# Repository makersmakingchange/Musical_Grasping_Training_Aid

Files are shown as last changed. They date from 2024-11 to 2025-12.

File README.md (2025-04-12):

# Musical Grasping Training Aid

## Overview

The Musical Grasping Training Aid is an assistive technology device that plays music when the device is grasped and pauses when it is let go. The user may upload their selection of songs onto the microSD card inside the device.

The device is comprised of off-the-shelf electronics and 3D printed parts.

The Musical Grasping Training Aid is open assistive technology (OpenAT). Under the terms of the open source licenses, the device may be built, used, and improved upon by anyone.

The overall cost of materials is about $90 (plus $5 for component shipping).

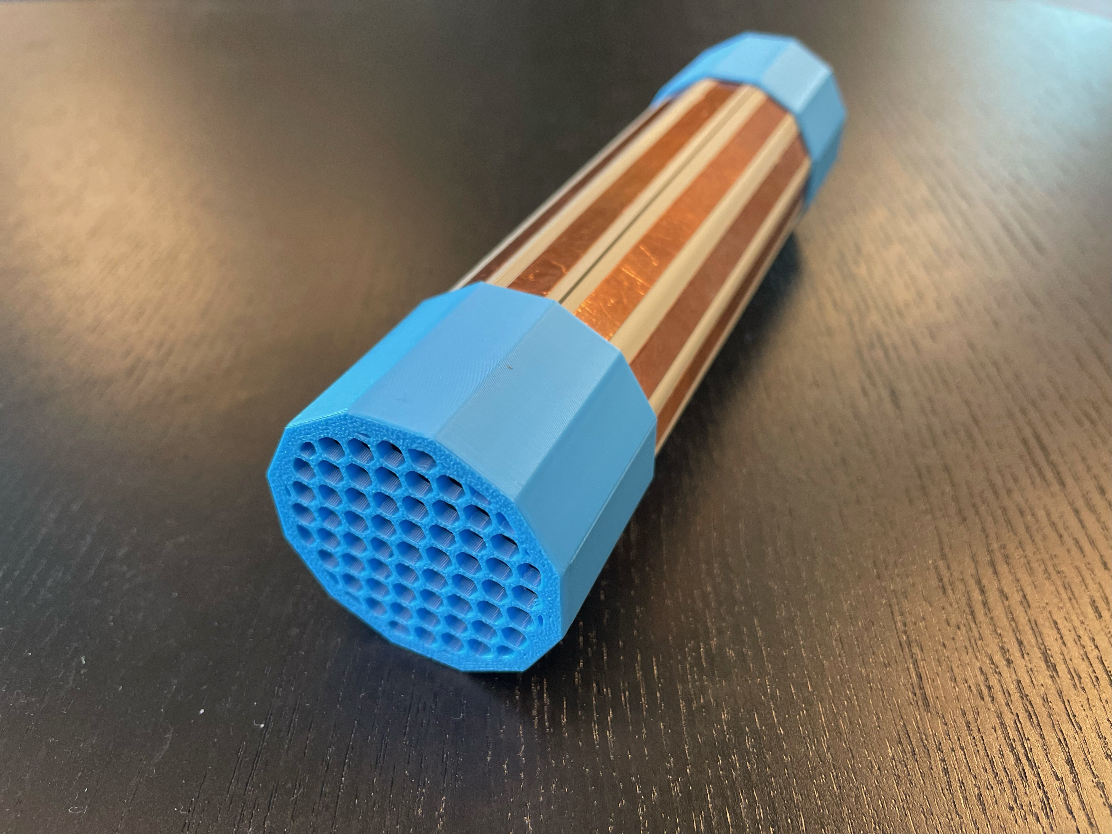
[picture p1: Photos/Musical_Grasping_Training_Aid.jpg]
Picture of Musical Grasping Training Aid.


## Makers Making Change Assistive Device Library
 - https://www.makersmakingchange.com/s/product/musical-grasping-training-aid/01tJR000007kNIXYA2

## How to Obtain the Device
### 1. Do-it-Yourself (DIY) or Do-it-Together (DIT)

This is an open-source assistive technology, so anyone is free to build it. All of the files and instructions required to build the device are contained within this repository. Refer to the Maker Guide below.

### 2. Request a build of this device

You may also submit a build request through the [Makers Making Change Assistive Device Library Listing](https://www.makersmakingchange.com/s/product/musical-grasping-training-aid/01tJR000007kNIXYA2) to have a volunteer maker build the device. As the requestor, you are responsible for reimbursing the maker for the cost of materials and any shipping.

### 3. Build this device for someone else

If you have the skills and equipment to build this device, and would like to donate your time to create the device for someone who needs it, visit the [MMC Maker Wanted](https://makersmakingchange.com/maker-wanted/) section.

## Build Instructions

### 1. Read through the Maker Guide

The [Maker Guide](/Documentation/Musical_Grasping_Training_Aid_Maker_Guide.pdf)  contains all the necessary information to build this device, including tool lists, assembly instructions, programming instructions and testing.

### 2. Order the Off-The-Shelf Components

The [Bill of Materials](/Documentation/Musical_Grasping_Training_Aid_BOM.csv) lists all of the parts and components required to build the device.

### 3. Print the 3D Printable components

All of the files and individual print files can be found in the [/Build_Files/3D_Printing_Files](/Build_Files/3D_Printing_Files/) folder.

### 4. Assemble the Musical Grasping Training Aid

Reference the Assembly Guide section of the [Maker Guide](/Documentation/Musical_Grasping_Training_Aid_Maker_Guide.pdf) for the tools and steps required to build the device.

## How to improve this Device
As open source assistive technology, you are welcomed and encouraged to improve upon the design. 

## Files
### Documentation
| Document             | Version | Link |
|----------------------|---------|------|
| Design Rationale     | 1.0     | [Musical_Grasping_Training_Aid_Design_Rationale](/Documentation/Musical_Grasping_Training_Aid_Design_Rationale.pdf)     |
| Maker Guide          | 1.0     | [Musical_Grasping_Training_Aid_Maker_Guide](/Documentation/Musical_Grasping_Training_Aid_Maker_Guide.pdf)     |
| Bill of Materials    | 1.0     | [Musical_Grasping_Training_Aid_Bill_of_Materials](/Documentation/Musical_Grasping_Training_Aid_BOM.csv)     |
| User Guide           | 1.0     | [Musical_Grasping_Training_Aid_User_Guide](/Documentation/Musical_Grasping_Training_Aid_User_Guide.pdf)    |
| Changelog            | 1.0     | [Changelog](CHANGES.txt)     |

### Design Files
 - [CAD Files](/Design_Files/CAD_Design_Files)

### Build Files
 - [3D Printing Files](/Build_Files/3D_Printing_Files)
 - [Firmware Files](/Build_Files/Firmware_Files)

## License
Copyright (c) 2024-2025 Neil Squire / Makers Making Change.

This repository describes Open Hardware:
 - Everything needed or used to design, make, test, or prepare the Musical Grasping Training Aid is licensed under the [CERN 2.0 Weakly Reciprocal license (CERN-OHL-W v2) or later](https://cern.ch/cern-ohl ) .
 - All software is under the [GNU General Public License v3.0 (GPL-3.0)](https://www.gnu.org/licenses/gpl.html).
 - Accompanying material such as instruction manuals, videos, and other copyrightable works that are useful but not necessary to design, make, test, or prepare the Musical Grasping Training Aid are published under a [Creative Commons Attribution-ShareAlike 4.0 license (CC BY-SA 4.0)](https://creativecommons.org/licenses/by-sa/4.0/) .

You may redistribute and modify this documentation and make products using it under the terms of the [CERN-OHL-W v2](https://cern.ch/cern-ohl).
This documentation is distributed WITHOUT ANY EXPRESS OR IMPLIED WARRANTY, INCLUDING OF MERCHANTABILITY, SATISFACTORY QUALITY AND FITNESS FOR A PARTICULAR PURPOSE.
Please see the CERN-OHL-W v2 for applicable conditions.

Source Location: https://github.com/makersmakingchange/Musical_Grasping_Training_Aid

## Attribution

The device was designed by Neil Squire Society / Makers Making Change. An [initial design](https://github.com/dbhaig/Musical_Toy) was created by Don Haig.

This design incorporates several commercially available open source hardware components from [Adafruit](https://www.adafruit.com/) and [DFRobot](https://www.dfrobot.com/). The Musical Grasping Training Aid firmware utilizes the [Arduino](https://www.arduino.cc/) development platform, and multiple libraries developed and shared by the open source community.

The documentation template was created by Makers Making Change / Neil Squire Society and is used under a CC BY-SA 4.0 license. It is available at the following link: [https://github.com/makersmakingchange/OpenAT-Template](https://github.com/makersmakingchange/OpenAT-Template)

### Contributors
 - Didi Dimitrova
 - Derrick Andrews
 - Stephan Dobri
 - Brad Wellington
 - Jake McIvor

----

<!-- ABOUT MMC START -->
## About Makers Making Change
[Makers Making Change Logo](https://www.makersmakingchange.com/)

Makers Making Change is a program of [Neil Squire](https://www.neilsquire.ca/), a Canadian non-profit that uses technology, knowledge, and passion to empower people with disabilities.

Makers Making Change leverages the capacity of community based Makers, Disability Professionals and Volunteers to develop and deliver affordable Open Source Assistive Technologies.

 - Website: [www.MakersMakingChange.com](https://www.makersmakingchange.com/)
 - GitHub: [makersmakingchange](https://github.com/makersmakingchange)
 - Bluesky: [@makersmakingchange.bsky.social](https://bsky.app/profile/makersmakingchange.bsky.social)
 - Instagram: [@makersmakingchange](https://www.instagram.com/makersmakingchange)
 - Facebook: [makersmakechange](https://www.facebook.com/makersmakechange)
 - LinkedIn: [Neil Squire Society](https://www.linkedin.com/company/neil-squire-society/)
 - Thingiverse: [makersmakingchange](https://www.thingiverse.com/makersmakingchange/about)
 - Printables: [MakersMakingChange](https://www.printables.com/@MakersMakingChange)

### Contact Us
For technical questions, to get involved, or to share your experience we encourage you to [visit our website](https://www.makersmakingchange.com/) or [contact us](https://www.makersmakingchange.com/s/contact).
<!-- ABOUT MMC END -->

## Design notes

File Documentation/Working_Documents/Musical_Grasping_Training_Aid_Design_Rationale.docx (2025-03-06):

# Introduction

Intentional grasp is an important developmental milestone for children. Toys that reward intentional grasping and holding could help with developing intentional grasping in various situations. An end-user requested a device which would reward grasping and holding the device, particularly by playing music while it is being held and stopping when it is put down.

This device can be for any user who is learning unimanual or bimanual coordination and grasping.

# Research

## Existing Commercial Options

Title | Baby Einstein Take Along Tunes
Link | https://www.amazon.ca/stores/BabyEinstein-Canada/page/9536BE3F-2738-48D2-830A-5A402E28861F?ref_=ast_bln
Author | https://www.kids2.com/pages/baby-einstein
License | Proprietary (Not open source)
Cost | $14.99 CDN (Amazon)
Notes | This toy does not sense when it is being held, just when buttons are pressed.

## DIY Designs

No comparable DIY designs were located.

# Requirements

## Goals

G01 | To motivate someone to pick up and hold an object by playing music while the object is being held.
G02 | Lightweight
G03 | Robust

## Functional Requirements

F01 | The device must be completely self contained (sound comes out of the device)
F02 | The device must play music when being held and stop when not being held
F03 | Users must be able to load their own music onto the device.
F04 | The device must be small enough for a child to hold (no larger than a toilet paper roll)
F05 | The device must be light enough for a child to hold

## Non-functional Requirement

NF01 | The device should be rugged enough to handle being dropped and possibly thrown by small children

## Constraints

C01 | Battery must deliver 5V (or just over) as lower voltages will be incapable of producing sufficient volumes in an audio amplifier, or audio module.

# Initial Design – Musical Toy

This design was originally taken on as a community design project. An initial design was created.

Title | Musical Toy
Link | https://github.com/dbhaig/Musical_Toy
Author | Don Haig
License | GNU GPL v3.0
Cost | Not given
Notes | This design is the basis for the musical toy and was used as the initial proof of concept and design.

The initial design was created by Don Haig and was uploaded to GitHub (https://github.com/dbhaig/Musical_Toy). MMC staff built and tested a prototype. This version was not sent to the original requestor. The original design used an Arduino Nano, a 9V battery, a small speaker, a DFPlayer, and a wire inserted into a 3D printed enclosure. The design was made using parts the original designer had on-hand or could order quickly online.

## Touch Sensing

The device worked by using a wire wound around the enclosure as a capacitive sensor. When the device was touched/picked up, lights would turn on and music would play. When it was released, the music and lights would stop.

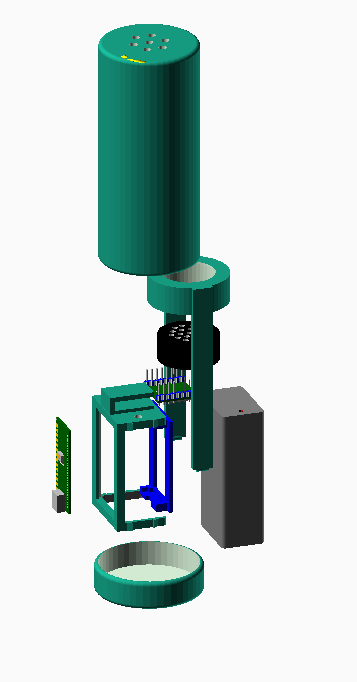
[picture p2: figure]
Exploded View

Figure 1. Exploded View

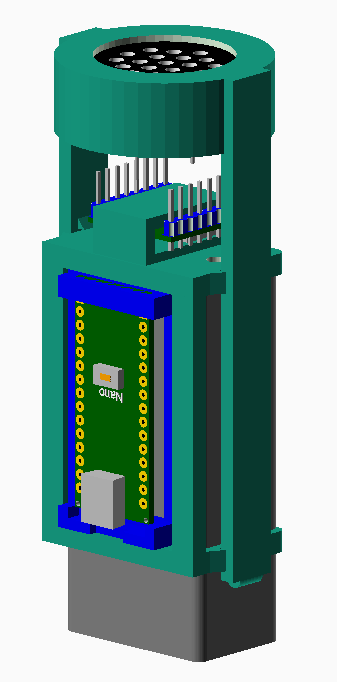
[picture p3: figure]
Interior Assembly

Figure 2. Inner Assembly

## Musical Toy Testing

The toy played music when activated, and would stop when deactivated, but the touch sensing did not work reliably. Depending on the sensitivity set within the code, it would activate before being touched (e.g., hand in proximity) or would not activate at all.

## Opportunities for Improvement

1. Use a smaller / less expensive microcontroller.
2. Using a smaller, more efficient power source than a 9V battery.
3. Inserting the wire into the case was difficult.
4. The outer enclosure is quite thin and may not be very durable.
5. Utilize a more reliable touch sensing method.

# Conceptual Design

The initial concept of the Conductive Music Player was to have a classic handheld flashlight tube shape. This tube would be small enough to be held by children, but big enough to hold batteries capable of powering the toy, for at least several hours.

## Key Functions

1. Plays Sound
2. Senses when gripped / lifted

## Playing Sound

1. DF Player Mini

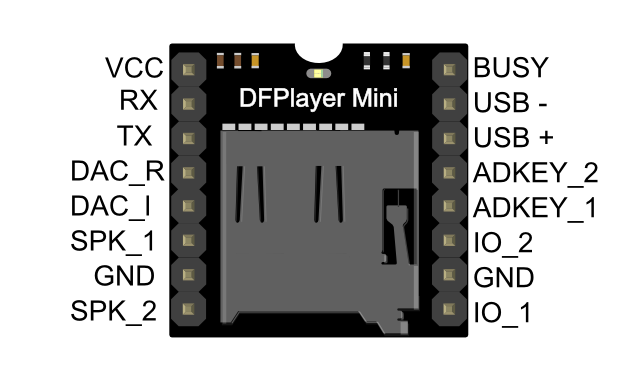
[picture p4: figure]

  - Integrated amplifier, microSD card
  - Fully supports FAT16, FAT32 file system, maximum support 32G of the TF card, support 32G of U disk, 64M bytes NORFLASH
  - A variety of control modes, I/O control mode, serial mode, AD button control mode
  - advertising sound waiting function, the music can be suspended. when advertising is over in the music continue to play
  - audio data sorted by folder, supports up to 100 folders, every folder can hold up to 255 songs
  - Low impedance speaker for good volume, with plastic cone/diaphragm for water resistance
  - Requires specific file naming
2. SD Player + Amplifier module (e.g., Open Playback Switch)
3. Adafruit Audio BFF Add-on for QT Py and Xiao
  - https://www.adafruit.com/product/5769
  - Has a built in amplifier and SD card but requires the analog pin from the microcontroller.
  - Product was not available when the project was started, but could be a good option for future improvements to the design

## Grip Sensing Method

### Capacitive Touch

1. Internal Microcontroller
2. Dedicated Module

The conductive music toy utilizes the Adafruit FreeTouch Arduino Library, which in turn, utilizes Atmel Q touch at the hardware level, on the micro controller chip.

Excerpt below, from: http://ww1.microchip.com/downloads/en/DeviceDoc/atmel-42195-qtouch-library-peripheral-touch-controller_user-guide.pdf

“Atmel® QTouch® Peripheral Touch Controller (PTC) offers built-in hardware for capacitive touch measurement on sensors that function as buttons, sliders, and wheels. The PTC supports both mutual and self-capacitance measurement without the need for any external component. It offers superb sensitivity and noise tolerance, as well as self-calibration, and minimizes the sensitivity tuning effort by the user.

The PTC is intended for autonomously performing capacitive touch sensor measurements. The external capacitive touch sensor is typically formed on a PCB, and the sensor electrodes are connected to the analog charge integrator of the PTC using the device I/O pins. The PTC supports mutual capacitance sensors organized as capacitive touch matrices in different X-Y configurations, including Indium Tin Oxide (ITO) sensor grids. In mutual capacitance mode, the PTC requires one pin per X-line (drive line) and one pin per Y-line (sense line). In self-capacitance mode, the PTC requires only one pin with a Y-line driver for each self-capacitance sensor.

Atmel® QTouch Features:

- Implements low-power, high-sensitivity, environmentally robust capacitive touch buttons, sliders, and wheels
- Supports mutual capacitance and self-capacitance sensing
- Up to 32 buttons in self-capacitance mode
- Up to 256 buttons in mutual capacitance mode
- Supports lumped mode configuration
- One pin per electrode - no external components
- Load compensating charge sensing
- Parasitic capacitance compensation for mutual capacitance mode
- Adjustable gain for superior sensitivity
- Zero drift over the temperature and VDD range
- No need for temperature or VDD compensation
- Hardware noise filtering and noise signal de-synchronization for high conducted immunity
- Atmel provided QTouch Library firmware and QTouch Composer tool”

#### Conductive Sensing Surface

Several options were considered for the conductive sensing material:

1. Conductive Cloth
2. Copper Tape
3. Embedded wire
4. Conductive paint
5. Conductive filament
6. Copper Foil

Conductive Cloth

The conductive cloth is a square of cloth plated with conductive material, such as silver. When someone touches the cloth, the capacitive touch library detects a change in capacitance of the cloth. The cloth offers low resistance (1 Ohm per foot of cloth), so the circuit can be more sensitive to touch. Additionally, the large surface area of the cloth allows the circuit to be more sensitive and reliable, as it is less likely that outside electromagnetic noise will influence the circuit than with embedded wires, which act like antennae. The conductive cloth also provides a soft surface for someone to touch, which may be desirable for some users. The cloth can be washed and cleaned as necessary.

Copper Tape

The copper tape is a roll of adhesive copper tape that will be stuck on the outer surface of the device to sense touch. When someone touches the tape, the capacitive touch library detects a change in capacitance of the tape. The copper tape is very thin and flexible allowing it to follow the surface shape.

Embedded Wire

The embedded wire follows a similar design to the copper tape, however, instead of being a flat adhesive strip it is a wire. The wire is sturdier and not as fragile as the tape, so it is more durable and can take on rough handling. The embedded wire would be attaches through small grooves into the device enclosure. Strips of wire can be attached to create a larger activation surface; however, it is important to be cautious that the embedded wire does not act like an antenna.

Conductive Paint

The conductive paint is a mixture of paint and carbon which creates a conductive coating on a surface. The paint is easy to apply with a brush, however, is difficult to clean and may chip away with long term use and rough handling.

Conductive Filament

Conductive filament is 3D printing filament that has combines a base plastic such as PLA with conductive additives to create a 3D printed conductive material. Unlike the other options listed, the conductive filament does not require anything to be attached to the outer surface of the device, as the enclosure itself will be conductive. The change in capacitance is sensed from the large activation surface of the device body. As conductive filament is not very common, this is reflected in the higher price point per roll of filament.

Copper Foil

Similar to the copper tape, the copper foil is a thin and flexible copper surface however, it does not have an adhesive surface. As the copper foil is a large copper sheet, it can be cut to the desired size and even wrapped along the entire outer surface if needed to. To attach the copper foil to the device, glue or another securing method will need to be used.

The conductive cloth offered a larger sensing surface area, which also increases sensitivity of the capacitive sensing.

### Linear soft potentiometer

A linear soft potentiometer was also considered for sensing touch. The potentiometer worked as a voltage divider and would output a different voltage based on where along its length the user was touching. The output voltage was 1/3 to 2/3 VCC.

https://www.adafruit.com/product/178

### Accelerometer

An accelerometer

#### LIS3DH

- Three axis sensing
- ±2g/±4g/±8g/±16g selectable scaling
- Both I2C (2 possible addresses) and SPI interface options
- Interrupt output
- Multiple data rate options 1 Hz to 5Khz
- As low as 2uA current draw (just the chip itself, not including any supporting circuitry)
- Tap, Double-tap, orientation & freefall detection

#### Accelerometer Additional Use Cases

As the accelerometer can sense varied motions with angle positions, and the micro controller can differentiate between them, it becomes possible to change device settings and behaviours based on this. As an example, the angle at which the device is positioned upon start up, can allow a user to set the sound to a specific volume. This can save parts in the product design, and the associated space and monetary costs those entail.

The ability to sense different user motion types should allow for various product behaviors, including:

- Setting volume (angle on device startup).
- Changing to a new song (shaking the device)
- Stepping up or down through a song list, or other list. (tilting device left or right)

Note that while using these methods can reduce device complexity and parts count, investments in software development, both in time and money, will be required upfront.

### Power Source

The toy was designed to be powered by battery, so it was portable. Disposable batteries were chosen for the initial design for simplicity. To meet the voltage demands of the electronics, four AAA batteries were used to supply 6V, and a voltage regulator was used to step this down to 5V for the electronics.

## Concept A: DF Player Mini + Accelerometer

Concept A used the DF Player Mini to read the SD card and play songs, and an accelerometer (Adafruit LISD3H) to sense when the toy was being held. The idea was to have the firmware track the stability of the readings from the accelerometer to differentiate between the toy sitting or lying stationary on a surface or being held. The assumption would be that even when a user was holding the toy still that the readings from the accelerometer would be more variable than when it was sitting or lying on a surface.

## Concept B: DF Player Mini + Capacitive Touch

Concept B was most similar to the original design by Don Haig but changed the method of capacitive sensing. Rather than using a wire wrapped around the case, a strip of copper tape and/or a conductive cloth is used for capacitive sensing.

## Concept C: DF Player Mini + Linear Soft Potentiometer

Concept C used a linear soft potentiometer to sense touch. The potentiometer worked as a voltage divider and would output a different voltage based on where along its length the user was touching. The output voltage was 1/3 to 2/3 VCC.

## Concept D: DF Player Mini + Capacitive Touch +Accelerometer

Concept D built off the original design by Don Haig. It used the DF Player Mini to read the SD card and play songs, and used capacitive touch sensing to detect when it was being held, and an accelerometer for extended options (such as changing songs). The accelerometer was used with tilting to change to the next or previous song based on how the accelerometer was tilted.

## Concept Selection

Concept D was selected for the prototype. We chose to include the accelerometer and capacitive touch sensing to increase future capabilities of the toy. The software for the capacitive touch sensing was simpler to develop and troubleshoot than it would have been to create the touch sensing with the accelerometer, but the accelerometer will allow for more complex controls and use cases in future developments with updates to the firmware.

The capacitive touch system was chosen over the linear soft potentiometer to increase the sensing surface of the toy. Either the soft potentiometer or using only a strip of copper tape would require a user to touch a smaller area of the toy to start it playing music. Using the conductive cloth allowed us to wrap more of the toy and decrease the likelihood of a user grasping the toy without activating it by missing the sensor. Additionally, the larger surface area increased the sensitivity and reliability of the capacitive sensing. The large piece of cloth was also the same price as the single linear soft potentiometer, and required only one resistor instead of three, decreasing the complexity of the circuitry and potential for errors when building the toy.

# Detailed Design

## Schematic

Add wire for conductive cloth (or copper tape) and a player busy line, to limit microcontroller interruptions.

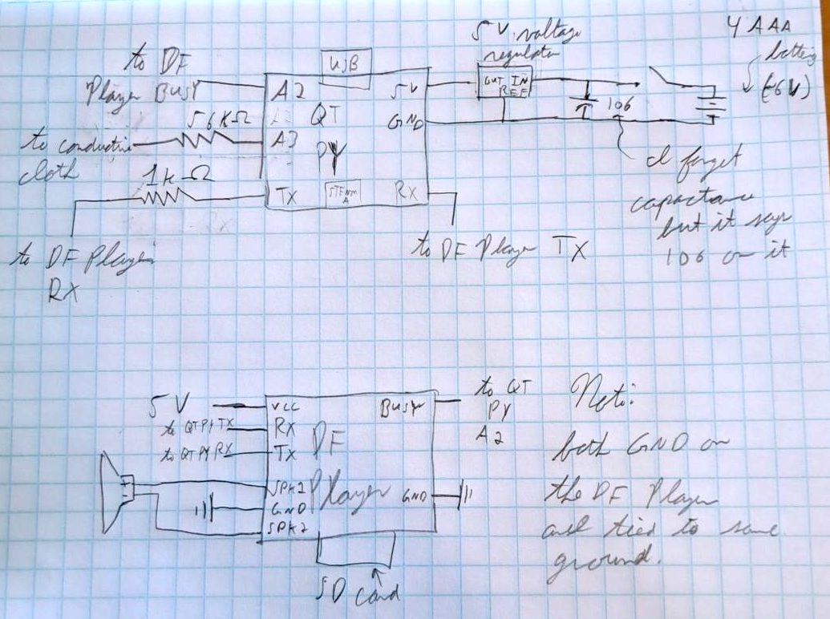
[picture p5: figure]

Figure 3. Schematic Sketch. Stephan Dobri.

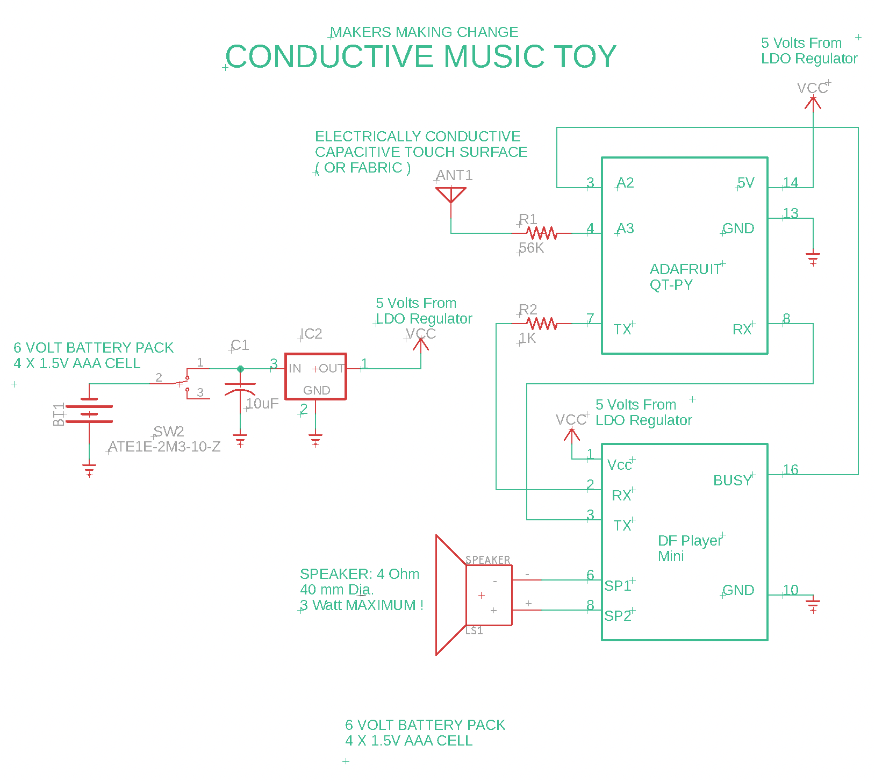
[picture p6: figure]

Figure 4. Electrical Schematic.

## Component Selection

### Microcontroller

Adafruit QTPY SAMD21

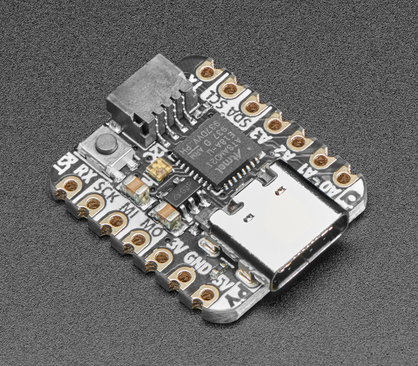
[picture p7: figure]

Figure 5. Adafruit QTPy SAMD21. CC SA-BY. https://learn.adafruit.com/assets/95170

### Speaker

Choosing the speaker for this design was relatively straightforward as the battery constraints and low voltage circuitry necessitates the use of low impedance speakers. Low impedance speakers are typically only available in 4 ohms, and 8 ohms from manufacturers. For a design, running on 3 to 5 V circuitry, 4 ohms is clearly the best choice, as higher voltages are required to drive 8 ohm speakers to a suitable volume level. As for physical size, a 40 mm speaker was chosen, as larger speakers would mean the toy would become too large for handheld use. The final choice was to use a plastic cone speaker rather than a paper cone, as a plastic cone can withstand water, and water-based, cleaners.

### Sound Module

The DFPlayer mini was chosen due to its sub miniature size, built-in 3 W audio, amplifier, and ability to be controlled by Arduino type microcontrollers. Additionally, the DFPlayer mini can except a microSD card within its own microSD card slot. This means that no external SD card reader is required. Finally, the DFPlayer is a very low cost, coming in at under $10.

The Sound Module connects to the microcontroller using a serial connection.

### Power Source Selection

The choice was made to go with a 6 V battery pack comprised of four AAA batteries. Batteries were an obvious choice, as the design is for a toy that will be carried around by small children. AAA batteries are available from most shops in both rechargeable and non-rechargeable types and are considered safer than lithium type batteries. Other readily available batteries, such as C and D type cell, are too large and heavy for a small carry around toy. The quantity of cells needed is determined by the volt, the voltage requirement of the circuitry. In this case, both the micro controller and the DFPlayer mini can be powered by 5 V. While the microcontroller can be driven by as little as 3 V, the DFPlayer requires a minimum of 5 V. Furthermore, battery ageing needs to be considered, so it’s better to start with a slightly higher voltage and regulate down to the desired voltage. In this manner, the circuit voltage remains stable. A small three pin 5V LDO regulator was chosen to trim the small excess voltage from the battery. An LDO (Low Drop Out) type regulator was chosen, as traditional voltage regulators usually stop working when the input voltage drops below the regulated output voltage. This allows the battery voltage to drop down to 4.5 V (the minimum required by the DFPlayer module) before the circuit stops working

### On/Off (power) switch

The slide switch was chosen to be as small as possible to be operated by a human finger. A 1-amp switch was chosen, as the circuitry in the Conductive Music Toy uses less than an amp. Larger switches would only be heavier and more expensive. An SPDT (Single Pole Dual Throw) type switch was selected, as it has a minimum of contacts to solder, while still being able change which side of the switch is considered as on or off.

### Accelerometer

The LISDH accelerometer from Adafruit was chosen for its low cost (under $10), small form, factor and ready availability from both Digi Key and Mauser electronics suppliers. While there are many suppliers that provide accelerometers with this description, we found that only the Adafruit version allows the device to be connected to a microcontroller via a solderless STEMMA type cable. This saves eight solder joints and the associated chance of wiring mistakes being made.

## Enclosure Design

### Shape

12 -sided

- Prevents rolling
- Feels more like a rounded handle

## Conductive Sensor

### Conductive Cloth Physical Attachment

The first design for attaching the cloth to the enclosure was to use metal snap fasteners. Two snaps would be attached to the enclosure, and the other snaps would be sewn onto the cloth. A wire was soldered to one of the snaps and ran into the enclosure to the 56k Ohm resistor in the above schematic, providing the electrical connection to the cloth. While the electrical connection worked with this method, the snaps could not hold two layers of cloth between them and would pop open very easily, so this method was abandoned.

The second method was to use adhesive backed hook and loop fasteners to attach the cloth to the enclosure. The adhesive backing was used to attach the fastener to the enclosure and onto the cloth. The cloth could then be attached to and wrapped around the enclosure. Since the cloth is difficult to solder, the electrical connection is created by a strip of copper tape on the outside of the enclosure to which the wire leading to the resistor is soldered. This method proved effective for the time being and is implemented in the prototype. There needs to be some long-term testing to assess how well the adhesive sticks to the cloth over time.

### Conductive Cloth Electrical Attachment

Wires soldered to snap

### Clothes vs. Tape

Cloth

- More to difficult to attach to handle
- More difficult to attach the electrical connection
  - Punch and snap required specialized hardware
  - Stainless steel conductive cloth hard to solder to
- Need to wrap around the enclosure – harder to open two-part split enclosure
- More difficult to clean

## Firmware

### Capacitive Touch Calibration

1. Sets baseline when first powered
2. Compares current value to adjustable threshold
3. Adjusting Volume

# V0.1 – Minimum Viable Product

## Summary

1. Total cost
2. Total print time / total number of printed components
3. (estimated assembly time)

## Features

1. Slide switch for controlling power
2. 4 internal AA batteries for power
3. 4 M3 screws to secure enclosure
4. Code adjustable volume
5. Supports 32GB SD card
6. Grasp and Play Operating Mode

### User Interface

Primary User

1. Lift to play music

Secondary User

2. Control power
3. Add / change songs by opening and modifying files on SD Card

Code

4. Adjust volume
5. Adjust capacitive touch sensitivity

### Operating Modes

1. Grasp and Play
  1.1. Cycling power resets to first file
  1.2. Grasping toy will cause music to play
  1.3. If grasped long enough, will cycle to next song
  1.4. If dropped, music will pause
  1.5. If grasped again, music will un-pause

## Internal testing

Testing while on battery power.

## Testing

(Any specific questions to address testing?)

1. Volume? Is there a need to adjust the volume
2. Adjusting volume with a potentiometer feeding an analog input.

## Opportunities for Improvement

1. Recess power switch?
2. Consider more secure cloth attachment method (integration into case, copper tape, glue, etc)
3. Recess enclosure-fastening screws
4. Simplify method / number of screws for opening enclosure
5. Investigate printability of sliding rails
6. Add accelerometer functionality

# V0.2 – Third Party Capacitive Touch Chip

Touch Sensor –

## Testing

3. Works on battery
4. Works by attaching wire from third party breakout board to copper tape on holder
5. (40 second recalibration time?)

# V0.3 – Third Party Capacitive Touch Chip

## Component Selection

### Touch Sensor – Adafruit MPR121 Module

The Adafruit MPR121 is a 12-channel capacitive touch sensor module with an I2C interface. The module is based on the MPR121 IC by Freescale Semiconductor. Intended for MP3 players, and other low-power, hand-held electronics. Power consumption for this chip is extremely low, coming in at 29 μA average supply current.

MPR121 Fact sheet: https://www.nxp.com/docs/en/fact-sheet/MPR121FS.pdf

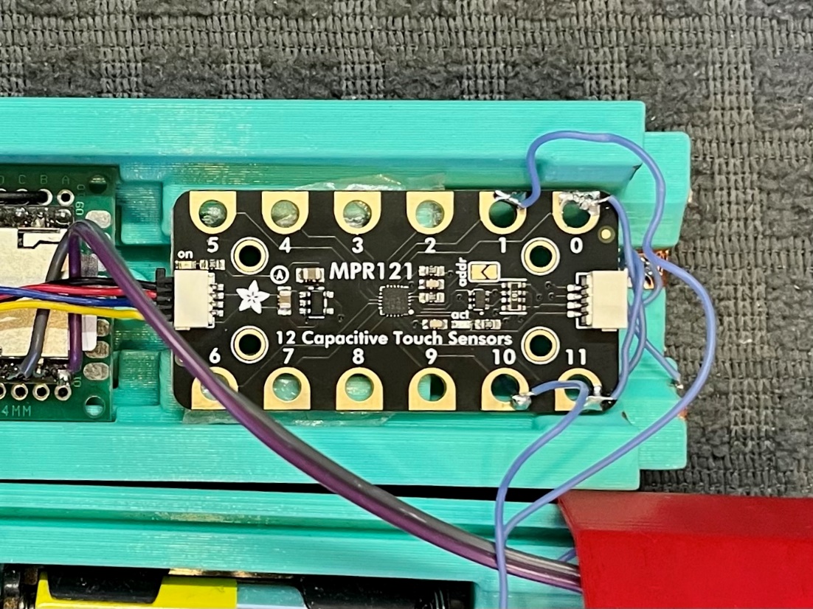
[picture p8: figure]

MPR 121 Module wiring:

The Adafruit MPR 121 module is connected to the QT-PY micro via a standard Stemma cable, which carries the basic I2C bus wires (Black=GND, Red =VCC Blue = Data Yellow = CLKor clock) The music toy has a set of 12 adhesive copper strips for touch sensing. The strips are wired together in four sets of three. A wire from each quadrant is then connected to one of the 4 input pads of the MPR-121.

Testing Questions

1. Activation on touch vs proximity? The Adafruit module activates, only on touch based on the testing that was done with the conductive music toy. This was done by approaching a finger to a capacity sensor pad and noting that the sensor did not trigger, even when the finger was within a millimeter of the touchpad. It was found that activation could occur through very thin paper or plastic material, however this this still “physical contact” sensation for a human finger.
2. Activation on contact vs grasp vs lifting? It is expected to be possible to differentiate between touching and grasping by taking advantage of multiple sensor, input, lines of the MPR 121. A single touch is unlikely to trigger multiple input lines simultaneously. A single touch is unlikely to trigger multiple input lines simultaneously. Therefore, grasping by hand can be assumed, if multiple input lines are triggered.

### Opportunities for Improvement

1. Modify enclosure
2. Add On/off label
3. External / easier access for MicroSD card?
4. Add accelerometer to better determine between grasping and lifting

### User Testing

The most recent version of the Conductive Music Toy was built and sent to the original requester, 4 years after the request was made. In the interest of getting, it to the tester as soon as possible, no changes were made to the SCAD enclosure to increase makeability. The existing enclosure was altered with a Dremel after printing to accommodate the parts, and it had to be fully glued shut once assembled.

A quick, basic, software implementation was written that covers the basic operating loop that the tester asked for, without any advanced grip detection or other advanced features.

### Maker Feedback

- Solder joints to copper tape are difficult and fragile
- Enclosure needs more room for wires/connections between components
- Enclosure needs a bit more tolerance between parts, especially when things such as copper taper are being inserted between them

### User Feedback

“Hi,

I'm sending a quick update with some feedback on the fun conductive music toy you've sent us for trial with my client - thank you again so much for hearing me out, finding a way to make this crazy idea happen and being open to feedback along the way.

Key observations so far:

-the size and shape seem pretty good. The diameter works fine for her hand - it's about the size of her hand railing on the stairs so works pretty well. I was initially a little worried it might be heavy for her but thus far she's not holding it independently and I suspect she can navigate it okay once she's really sustaining her grasp longer to carry it with her. Probably wouldn't want it to be too much heavier.

-sound level: it's a bit loud - we stuck a sock on the end at times to lower the volume

-music loaded: it took us a little while to realize that we could just hold it for a long time to get the songs to advance and change. Seems that when we turn it off, it resets to the first song. Now that we know this, we can play around with it and hold it for awhile to get it to a new song that lights up her reaction!

-touch functionality: for some reason when it's initially turned on it takes a little time to warm up and feel good about its existence - it helps to have an adult muck about with it for a few minutes to help it warm up and be responsive to her touch

wish list items:

-stand system: I'm going to try (?) to make a little stand for it to keep it in a vertical upright position as this makes it easier for her to grasp - like a docking system that allows her to pick it up in that vertical orientation. I'll probably try a little foam or cardboard - a 3D printed thingy in the future that fits would be cool. Right now, she holds it best when we hold the end portions (VERY HELPFUL feature - as this allows us to hold it up in place and NOT activate it, waiting for just HER touch to activate it).

She's most often using her hands to grasp it well when she is using it to stabilize herself - so picture that she's on a physio ball with some hands on help from me - I challenge her balance a little and she reaches out to the conductive toy to stabilize herself - I'm holding it up in the air for her to grab - she had some GREAT visual looks to it and smiles when the music activated. She needs lots of time with this to keep building her recognition of it and understanding of its cause/effect function.

-long term usage: as noted when you sent it, being able to charge the battery and change the music stored on it through a port would be great

-it'd also be great to have a way to advance the songs with a single button (for the adult to do, so not needed to be special for kid) - thinking here that her music interests change quickly and it's really helpful for her when we change the song up!

Again - I want to send a really big thank you to the team for this opportunity - it feels really good to have a new idea to support this kid, help her light up and teach her something new with something that literally does not exist out there in the world.

THANK YOU!

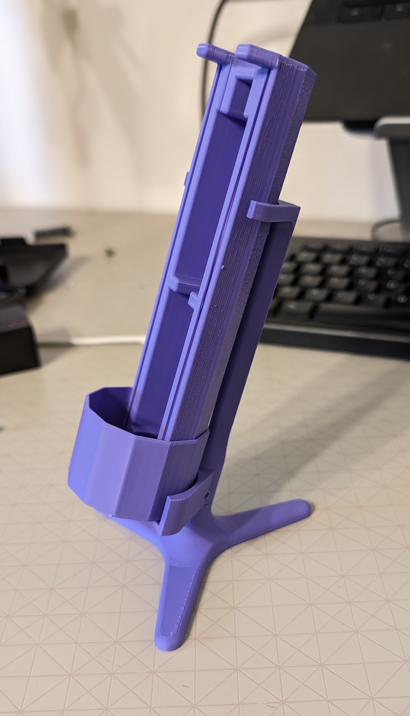
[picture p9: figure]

### Follow Up User Meeting

Brief follow up meeting with the user to talk about the feedback given and get some more detail

- Song skip button to keep it fresh
- Made a stand to hold the device upright
- Want the volume turned down a bit, but user volume adjustment is not a priority
- Startup issues may be due to users touching the tape while turning it up and skewing initial calibration

### Next Steps

- Improve enclosure
- Add ability to change batteries/charge the device
- Add the ability to change songs loaded on the device
- Add a recessed switch to skip to the next song without letting it play all the way through
- Secondary-user accessible volume control

# V1.0 Musical Grasping Training Aid

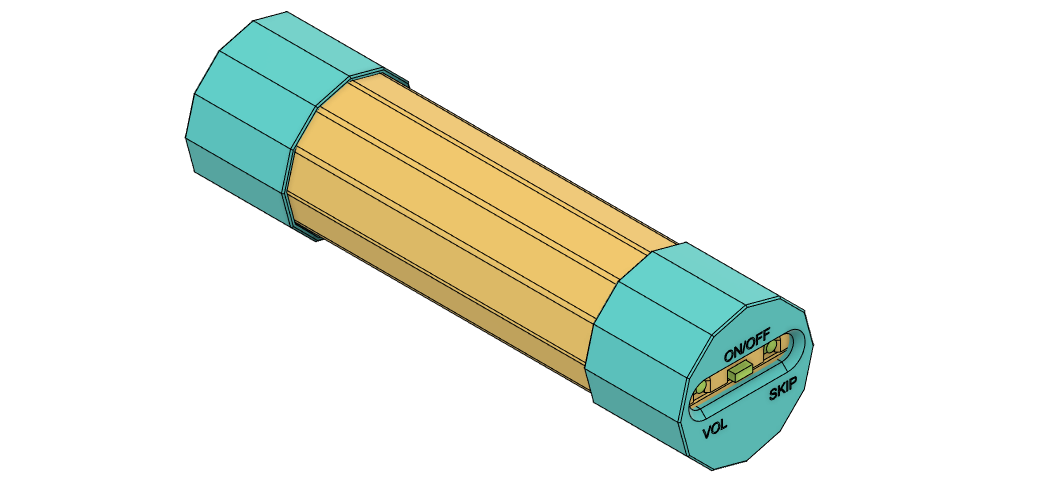
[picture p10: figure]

## Proposed Changes

1. Improve make ability and usability of enclosure
  1.1. Add ability to change batteries
    1.1.1. Integrating a commercially available battery holder
    1.1.2. Creating a 3d printed battery holder and use commercially available battery contacts
      1.1.2.1. Copper tape?
  1.2. Power switch
  1.3. Add a recessed switch so secondary user can skip to the next song
    1.3.1. (Currently the only way to advance the song is to activate the device and wait until the entire song plays)
  1.4. Secondary user access to the SD card to change songs
    1.4.1. Sufficient instructions for reasonably tech savvy user to remove SD card, connect to computer, load songs using specified numbered file format, replace SD card
  1.5. Consider adding secondary user accessible control for adjusting volume
    1.5.1. 1 button
      1.5.1.1. toggle through levels
      1.5.1.2. short press / long press
    1.5.2. 2 two buttons – volume up / volume down
    1.5.3. Potentiometer?
    1.5.4. Using the touch sensor / other existing input to control volume
  1.6. Ensure sufficient clearance for cables, etc.
  1.7. Maintain diameter
  1.8. Maintain or reduce weight
2. Documentation
  2.1. User Guide
3. Component Changes
  3.1. Bluetooth-enabled microcontroller (e.g., XIAO nrf52840)
    3.1.1. Training Aid + Smartphone App
    3.1.2. Training Aid + Bluetooth Microcontroller
  3.2. Alternate Music Player
    3.2.1. Adafruit Audio BFF Add-on for QT Py and Xiao (https://www.adafruit.com/product/5769)

## Requirements

### Goals

G01 | To motivate someone to pick up and hold an object by playing sounds while the object is being held.
G02 | Lightweight
G03 | Robust
G04 | The ability to continue to motivate the user
| A secondary user (e.g., therapist, aide, caregiver, parent) must be able to adjust some settings on the device.

### Functional Requirements

F01 | The device must be completely self contained (sound comes out of the device)
F02 | The device must play music when being held and stop when not being held
F03 | Users must be able to load their own music onto the device.
| User must be able to periodically change the music on the device.
F04 | The device must be small enough for a child to hold (no larger than a toilet paper roll)
F05 | The device must be light enough for a child to hold.
| A secondary user must be able to control the power state of the device.
| A secondary user should be able to control the volume of the device
| A secondary user should be able to skip to the next song.
| A secondary user should be able to access the device controls without the use of tools.
| The primary user should not be able to access the controls.
| The secondary user must be able to change the batteries.
| The primary user must not be able to access the batteries. | Safety
| The secondary user should be able to access the batteries without tools. | Convenience

### Non-functional Requirement

NF01 | The device should be rugged enough to handle being dropped and possibly thrown by small children

### Constraints

C01 | Battery must deliver 5V (or just over) as lower voltages will be incapable of producing sufficient volumes in an audio amplifier, or audio module.
C02
C03

## Design Features

| Version V0.3 (MVP) | Version V1.0
User Interface | On/Off Button | On / Off Button Volume Control Ability to skip songs
Battery Access | None (enclosure glued shut) | Accessible by secondary user
Capacitive Sensor Calibration | Auto-calibration (Just on startup or continuously?) | Auto-calibration
SD card Access | None (enclosure glued shut) | Accessible by secondary user

### User Interface Brainstorm

V0.3

- Power switch accessible on the end cap
- Power switch is partially recessed into the end cap

V1.0

- User interface elements

User Interface Options

1. Recessed / partially recessed into the enclosure or end cap
2. Removable or openable panel or cover that prevents the primary user from accessing them
3. ~~(~~~~Wireless / secondary device)~~

### Music Control

V0.3

- Always starts at the beginning of the playlist of songs when the device is turned on.
- There is no user control to skip songs.
- When activated, current song plays. When let go, music pauses. When unit is re-activated, music continues to play

V1.0

Song Control Options

1. No control – starts at first song, only way to advance is to activate it
2. One additional control for skipping songs
3. Two additional controls for skip ahead / go back.
4. ~~(accelerometer-based gesture / shake)~~

### Volume Control

V0.3

- Volume is adjustable by code
- Volume is limited by physically covering the speaker (e.g., with a sock)

V1.0

- Secondary user volume control

Volume Control Options

1. Single tactile button that cycles through volume levels
2. Capacitive touch area (i.e., utilize one of the channels on the cap-sense board)
3. Potentiometer that is adjusted by screwdriver
4. Potentiometer that is adjustable by hand

### Music Loading

V0.3

- MicroSD card is pre-loaded with set of music and then glued into the enclosure

V1.0

- User-accessible method for changing the set of songs that are loaded on the device

Music Loading Options

1. MicroSD card is removable by the secondary user
2. Some method for attaching the device via USB cable
3. Wireless loading of music

### Battery Access

V0.3

- Sliding enclosure; requires complete disassembly
- (Glued shut)

V1.0

- Accessible by secondary user with up to one screw

Battery Access Options

1. Flashlight-style slide-in
2. Remote-control style side insertion / sliding / snap fit cover
  a. Challenging with need for capacitive copper tape on the outside
3. ~~(Built-in~~ ~~/ non-removable~~ ~~Lithium batteries)~~

### Architecture

V0.3

- Two hollow cylinder halves
- Sliding connection
- Speaker cap press fit on
- Switch cap attached with screws

V1.0

- Two hollow cylinder halves
- Sliding connection
- Speaker cap press to fit on
- Switch cap attached with screw

Architecture Options

1. Two halves + end caps
2. Hollow tube + insert.

## Features

- On/off switch to control device
- Two push buttons (one for volume control and another for song skipping)
- Removable cap to allow for battery access

## User Interface

### Primary User

- Grasp to play music

### Secondary User

- Sliding power on/off switch
- Change volume
- Skip song
- Change Batteries
- Change songs on microSD

### Code

- Adjust capacitive touch sensitivity
- Adjust volume level presets

## Operating Modes

1. Grasp and Play
  1.1. Cycling power resets to first file
  1.2. Grasping toy will cause music to play
  1.3. If grasped long enough, will cycle to next song
  1.4. If dropped, will pause
  1.5. If grasped again, music will un-pause
  1.6. If left button is pressed, the volume will cycle through presets
  1.7. If right button is pressed, the song will be skipped, and the next one will play

## Testing

1. Skip Button works
2. Volume Button works and cycles through 6 volume settings (1 press = next volume setting and it starts at the lowest volume, 5)

## Touch Sensing

### Copper Tape

The device uses 12 strips of copper tape along the edges of the outer surface of the device enclosure. The 12 strips are split into four quadrants (3 strips attached together per quadrant) and soldered into pins 0-3 of the MPR121 capacitive touch sensor module. To play music, two or more of the four capacitive touch sensor pins must be activated above the defined threshold value. This helps differentiate when the device is grasped as opposed to just being touched. Grasping the device requires more than one of the copper quadrants to be activated at the same time whereas, touching actives just one quadrant. Of course, if the device is being touched with multiple fingers to activate multiple quadrants, then this may cause the device to play music when it is not grasped. This is an area with room for improvement for future versions which can incorporate an accelerometer to further distinguish between grasp and touch.

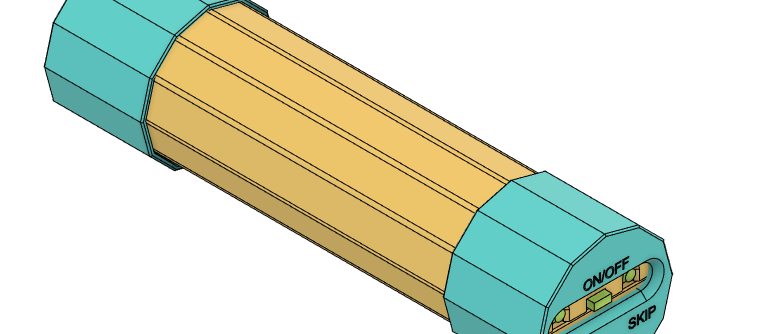
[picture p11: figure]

# Detailed Design

## Concept Sketch

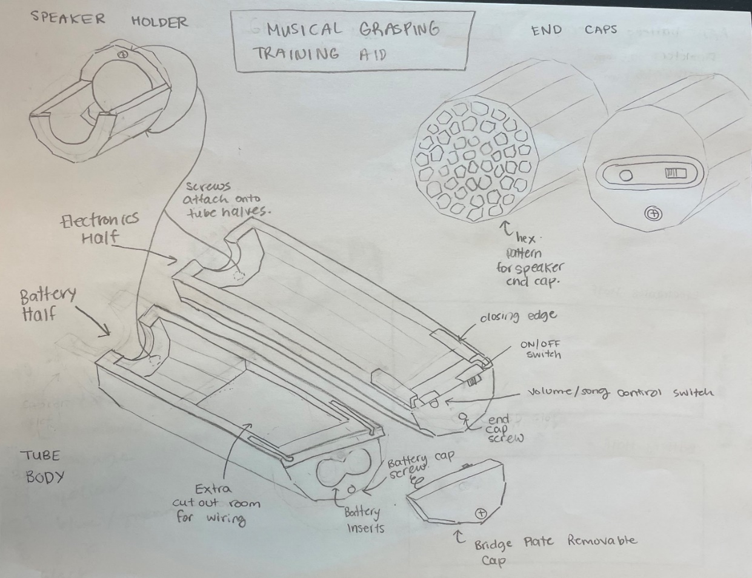
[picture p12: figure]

## Schematic

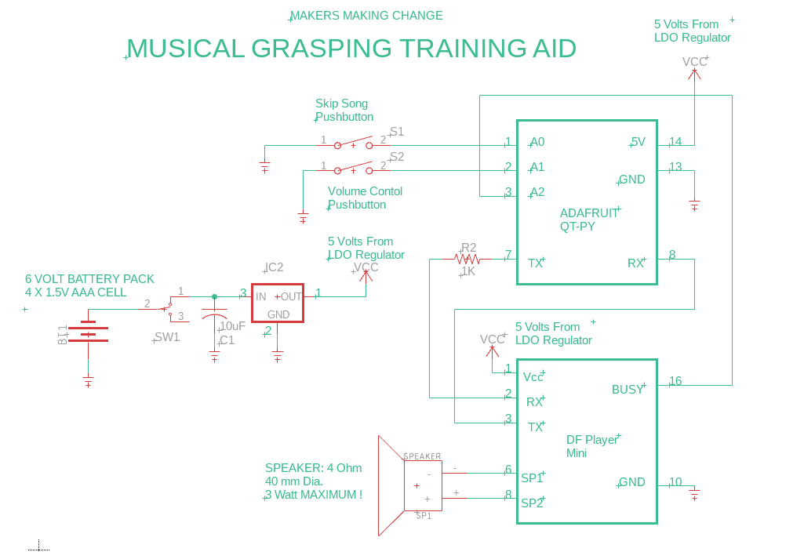
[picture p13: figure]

## Component Selection

### Battery Clips

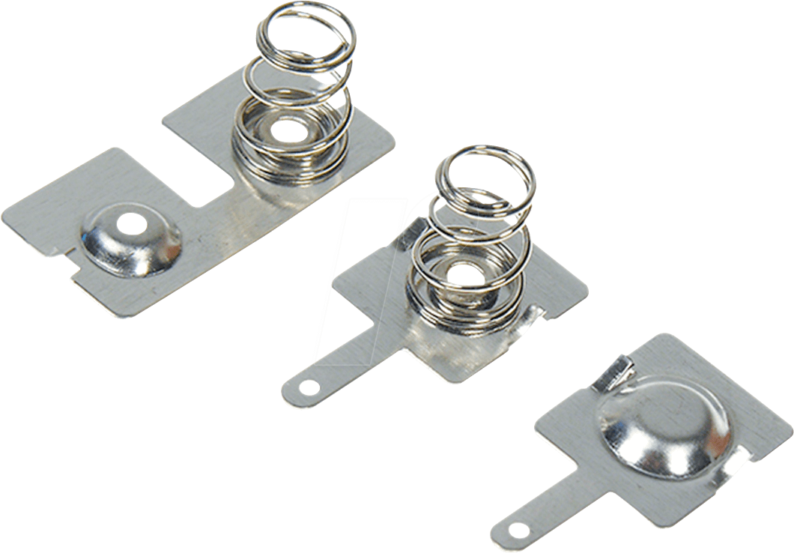
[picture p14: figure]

The battery clips in this new version replace the two AAA battery holders. They will be used to create a built-in battery compartment within the device to let the user replace the batteries when needed. The bridged endplate will be place on the cap that closes the compartment while the other two will be attached to the inside of the battery compartment. These clips are small and lighter than the battery holders and allows for easy access to the batteries, like a flashlight.

### Updated Adafruit MPR121 module

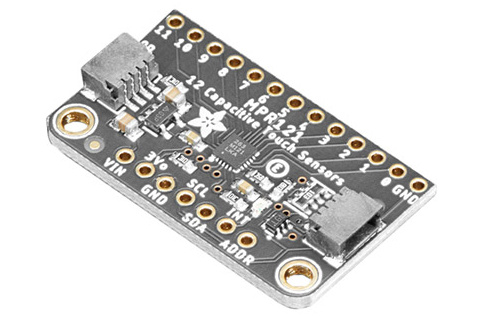
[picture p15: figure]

The MPR121 capacitive touch sensor module was updated with this new version, which has the same functionality as before but is significantly smaller. The board’s small size increases the room inside the device which will help make additional room for wiring. The capacitive touch sensor is still connected to the QT-PY microcontroller using a standard Stemma cable. The copper tape attached to the outer surface of the device enclosure is split into four quadrants, each quadrant being attached with a wire from pins 0-3 on the MPR121 module.

## Enclosure Design

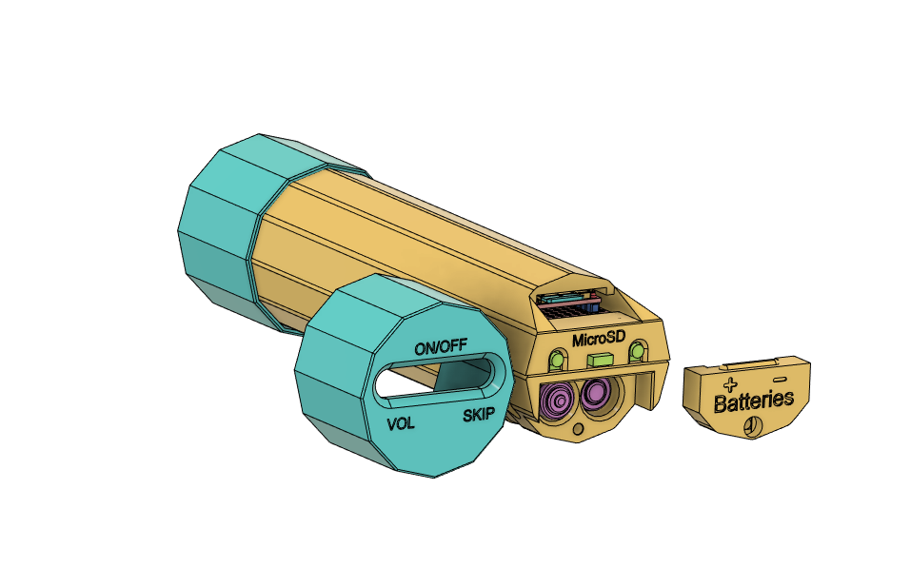
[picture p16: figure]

### Battery Compartment

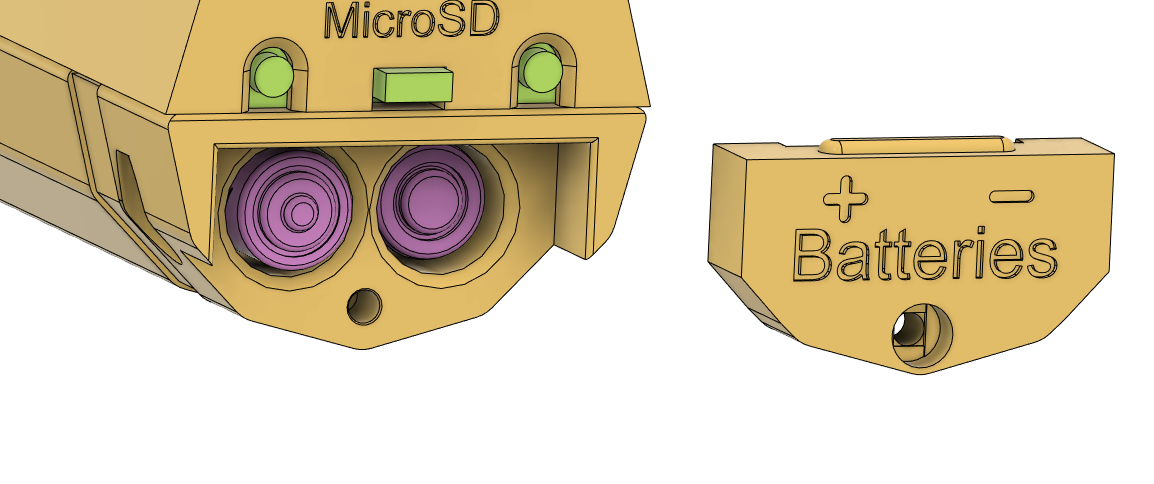
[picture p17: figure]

### MicroSD Card Slot

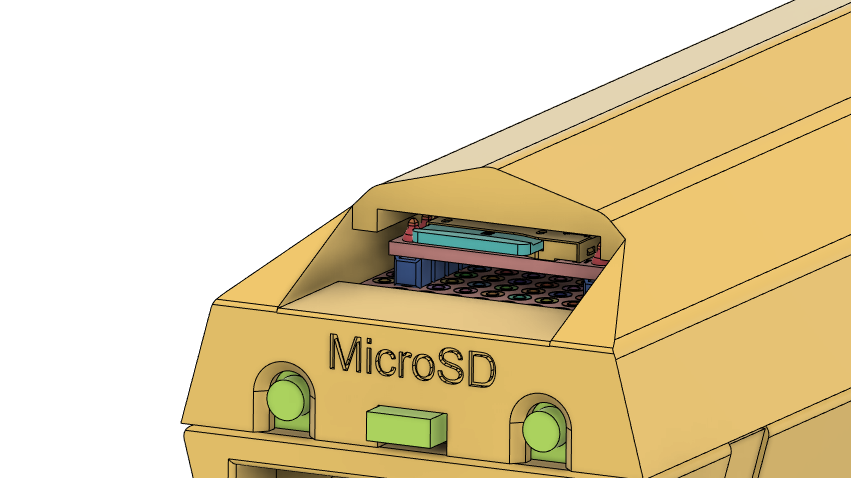
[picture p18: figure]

### Volume Control and Skip Buttons

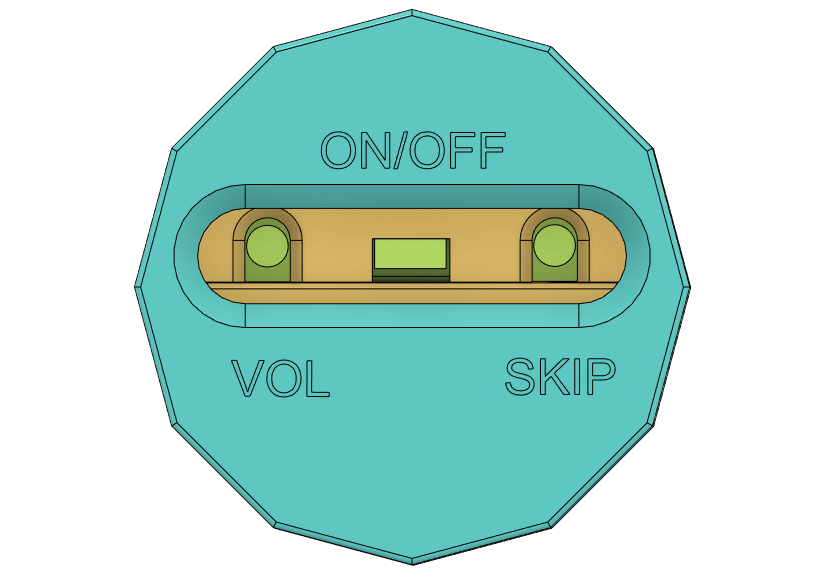
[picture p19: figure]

## Firmware

### Capacitive Touch Calibration

1. Sets baseline when first powered
2. Compares current value to adjustable threshold

### Adjusting Volume

1. Choose 6 different volume levels to cycle through using push button. The volume levels are 5, 8, 11, 14, 17, 20 but can be modified, and restart once fully cycled through.
2. The volume that the device starts playing music at is 5 when turned on.

### Activation

The Musical Grasping Training Aid uses copper tape strips which are organized into quadrants (3 connected strips in each quadrant) to create an activation surface. When one of these quadrants is touched and the MPR121 capacitive touch sensor reads a value above 1, the music will begin to play. This version of the device adopts an all or nothing approach to determine when the device is being grasped. Reading a value of 0 means that the device is not touched and once a value of 1 is detected, the music will begin to play. The threshold value can be altered to increase or decrease the sensitivity (an approach that can be explored in future iterations of this device).

## User Feedback

Hi!

Sorry for my slow response. Nothing happens quick over here it seems. Thank you for your continuing work on this cool project!

I'll answer your questions as best as I can here: (questions are bolded and answers are normal)

1. How are you finding the stand that was designed for the Conductive Music Toy? Does it work well with the device or does the size, shape and/or orientation need to be modified? I think the stand works well. Because of its lightweight I think it needs some Velcro to attach it to the surface of where it lives. <CLIENT>'s gross motor movements are pretty aggressive sometimes when reaching for things, so she knocks it over regularly if reaching for it. But I think some Velcro will work great.
2. Do you think the battery access design will improve your user experience with the device? If not, do you have any alternative recommendations to the proposed design? I think battery access would be great or if it’s a rechargeable battery, then having a USB charging port would be good as well. Either system would work well, I think.
3. Do you think the microSD card access design will improve your user experience with the device? If not, do you have any alternative recommendations to the proposed design? Yes, I think microSD would certainly help us as the need to continually update the music is integral as <CLIENT>'s music preferences change often. Alternatively, a USB port that could allow the device to be connected to a computer to delete and upload new music files directly would be potentially easier and less steps for the user.
4. Do you think the volume button feature will improve your user experience with the device? If not, do you have any alternative recommendations to the proposed design? A volume button would be most useful as different environments pose different listening challenges. In a quiet room the current volume of the unit is too loud.
5. Do you think the song skipping button feature will improve your user experience with the device? If not, do you have any alternative recommendations to the proposed design? Yes, I think having the ability to skip tracks and find the most motivating music on the playlist quickly would be ideal.

I think that covers all the notes we had for it. Excited to see the next version!

Thanks again to everyone working on this. Very cool!

## Opportunities To Improvement / Future Work

Activation Method

An alternative method that combines the four quadrants and a minimal activation threshold value to differentiate between touch and grasp can be explored. This method would continue to have four copper tape quadrants (3 connected strips each), but only play music when two or more quadrants are activated above a certain threshold value. A threshold value would need to be determined through research and experimentation to ensure that it is not too low or too high.

© 2023-2025 by Neil Squire Society / Makers Making Change. This work is licensed under the CC BY SA 4.0 License: http://creativecommons.org/licenses/by-sa/4.0 Files available at https://github.com/makersmakingchange/Musical_Grasping_Training_Aid Page 1 of 1

V1.0 | September 2024 Conductive Music Toy Design Rationale

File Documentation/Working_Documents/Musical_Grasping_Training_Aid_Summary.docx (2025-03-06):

# Overview

The Device Summary is intended to be a detailed summary of the device, product and maker information for the Musical Grasping Training Aid, making it easier to add to the Makers Making Change website. It is intended for anyone who will view the device listing.

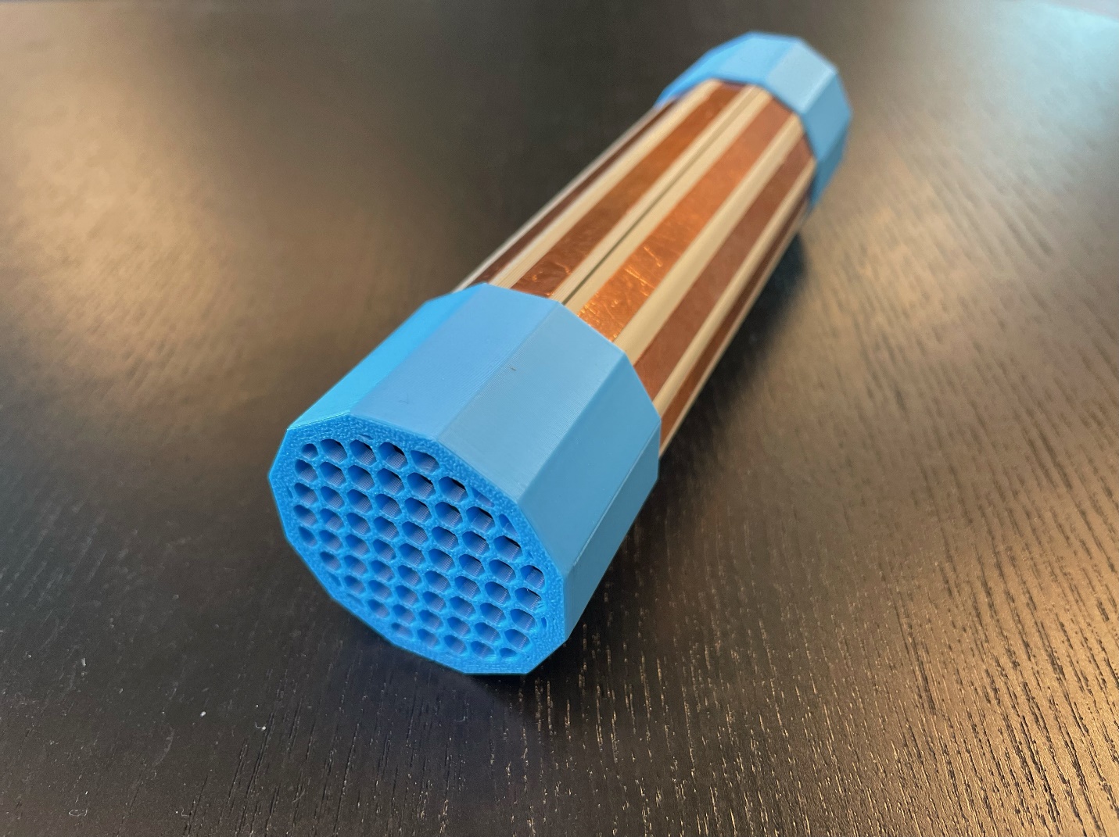
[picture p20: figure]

# Product Information

## Product Name

Musical Grasping Training Aid

## Device Category

Mark any relevant categories with an “X”:

| Adapted Toys
| Aids for Daily Living (ADL)
| Assistive Switches
| Communication Aids (AAC)
| Computer Access
| Environmental Controls
| Gaming
| Keyguard
| Kits
| LipSyncs
| Mounting
X | Recreation and Leisure
| Seating and Positioning
| Switch Interfaces
| Writing Aids

## User Value Statement

Encourages individuals with neurodevelopmental differences to use hands and learn cause and effect through grasp activated musical play.

## Designer

Makers Making Change

# Device Information

## Overview

The Musical Grasping Training Aid is designed to encourage grasping and holding and learn cause and effect. When a user holds the device, it plays music and when the device is not being held, it pauses the music. Users can upload their own music onto a microSD card inside the device and upload new or additional songs when they are no longer motivated by the current selection of songs.

## Disability Type

Select one or more disability types and mark with an “X”:

| Agility / Dexterity
| Arthritis
X | Cognitive
| Hearing
| Mobility
| Pain
| SCI
| Vision
| Other

## Disability Type Description

This device is intended for people with neurodevelopmental differences and individuals who are trying to learn the concept of cause and effect.

## How To Use

Power On

To power on the device, flip the switch on the side of the device from OFF to ON.

Setup

After turning on the power switch, wait a few minutes for the device to calibrate. To properly calibrate the device, make sure it is placed in the stand, and it is not being touched.

Musical Grasping

After calibration, the device is ready to be used. The device senses grasp through the copper tape along the tube of the body and will only play music if it is being grasped along this surface. To play the music loaded onto the device, grasp the copper tape activation surface on the device. Note, the device will not play music if it is being grasped by the end caps.

Once the device is no longer held and let go, the music will pause and stop playing. To continue playing music, the user must grasp the device again.

Volume Control

To change the volume of the music being played, press the left button on the side of the device (above the VOL label). The device has six volume levels (5, 8, 11, 14, 17, 20), and each press cycles to the next volume setting. When calibrated, the device starts at level 5 and will cycle through the remaining levels. If the volume button is pressed while the device is playing music at the last level, it will restart to play music at the first volume level.

Song Skip

To skip a song, press the right button on the side of the device (above the SKIP label). This will skip to the next song loaded onto the microSD card inside the device. If the skip button is pressed while the last song is played, the device restarts the song list and plays the first song.

## Estimated Cost

The estimated material cost of the device for a single build:

| $0 - $10
| $11 - $25
| $26 - $50
X | $51 - $100
| $101 - $250
| $250+

## Attribution

Designed by Neil Squire / Makers Making Change. An initial design (https://github.com/dbhaig/Musical_Toy) was created by Don Haig.

Contributors:

- Didi Dimitrova
- Derrick Andrews
- Stephan Dobri
- Brad Wellington
- Jake McIvor

This design incorporates several commercially available open source hardware components from Adafruit (https://www.adafruit.com/) and DFRobot (https://www.dfrobot.com/). The Musical Grasping Training Aid firmware utilizes the Arduino (https://www.arduino.cc/) development platform, and multiple libraries developed and shared by the open source community. Full details are available on GitHub (https://github.com/makersmakingchange/Musical_Grasping_Training_Aid).

# Maker Information

## Project Skills

Mark the required project skills with an “X”:

X | 3D Printing
| Custom PCB
X | Electronics
| Laser Cutting
| Mechanics
X | Software
X | Soldering
| Woodworking
| Other

## Skills Description

This is an advanced build that requires careful soldering of components to a protoboard and flashing firmware.

## Tools Needed

X | 3D Printer
X | Common Hand Tools
| Common Power Tools
| Laser Cutter
X | Soldering Iron
| Specialized Tooling

## Print time (hrs)

3.90

## Assembly time (hrs)

4.00

## Build Instructions

This build consists of a number of off-the-shelf electronic components that are soldered onto a protoboard and assembled into a 3D printed enclosure. Firmware is then flashed to the microcontroller.

For full instructions, please refer to the Maker Guide.

## Download Link

## https://github.com/makersmakingchange/Musical_Grasping_Training_Aid/archive/refs/heads/main.zip Project Link

https://github.com/makersmakingchange/Musical_Grasping_Training_Aid

# License

## License

- Everything needed or used to design, make, test, or prepare the Open Playback Recorder is licensed under the CERN 2.0 Weakly Reciprocal license (CERN-OHL-W v2) (https://cern.ch/cern-ohl) or later .

- All software is under the GNU General Public License v3.0 (GPL-3.0) (https://www.gnu.org/licenses/gpl.html).

- Accompanying material such as instruction manuals, videos, and other copyrightable works that are useful but not necessary to design, make, test, or prepare the Open Playback Recorder are published under a Creative Commons Attribution-ShareAlike 4.0 license (CC BY-SA 4.0) (https://creativecommons.org/licenses/by-sa/4.0/).

© 2024 by Neil Squire This work is licensed under the CC BY SA 4.0 License: http://creativecommons.org/licenses/by-sa/4.0 Files available at https://github.com/makersmakingchange/Musical_Grasping_Training_Aid Page 1 of 2

V 1.0 | September 2024 Musical Grasping Training Aid Summary

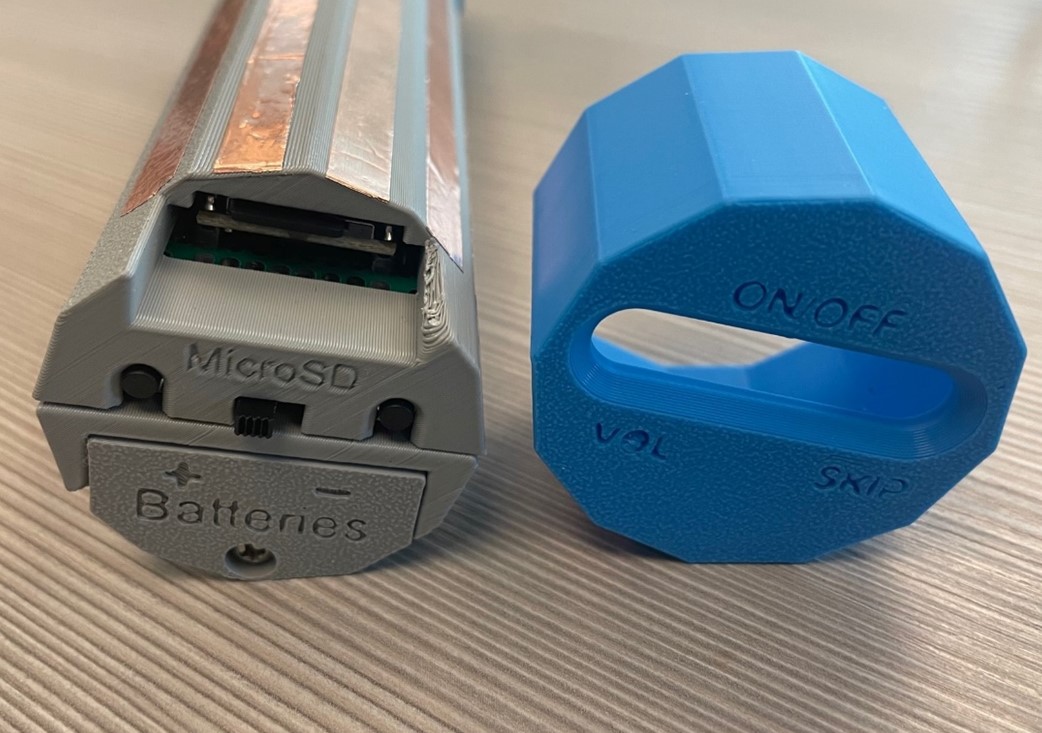
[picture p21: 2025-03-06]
Photos/Musical_Grasping_Training_Aid_User_Interface.jpg

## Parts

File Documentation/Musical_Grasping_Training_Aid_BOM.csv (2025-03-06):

Device: | Musical Grasping Training Aid
Version: | V1.0
Last Updated: | 2024-12-18
 |  |  |  |  |  |  |  | Total filament (g) |  | Unit Cost | Total Estimated Cost
 |  |  |  |  |  |  |  | 101 |  | $90.48 | $90.48
ID | Commercial Parts |  |  |  |  |  |  |  |  | $87.95 | $87.95
 | Part | Description |  | Manufacturer | Supplier | QTY / Device | QTY / PKG | PKGs | $/ PKG | $ / Device | Total Estimated Cost | Link
A01 | 30x70mm Proto Board |  |  | Adafruit Industries LLC | digikey | 1 | 1 | 1 | $4.25 | $4.25 | $4.25 | https://www.digikey.ca/en/products/detail/adafruit-industries-llc/4784/13617526
A02 | Adafruit QT Py microcontroller | SAMD21 with STEMMA QT |  | Adafruit Industries LLC | digikey | 1 | 1 | 1 | $10.80 | $10.80 | $10.80 | https://www.digikey.ca/en/products/detail/adafruit-industries-llc/4600/13543375
A03 | DFRobot DFPlayerMini | Mini MP3 Player |  | DFRobot | digikey | 1 | 1 | 1 | $8.50 | $8.50 | $8.50 | https://www.digikey.ca/en/products/detail/dfrobot/DFR0299/6588463
A04 | 1K Ohm Resistor |  |  | Stackpole Electronics Inc | digikey | 1 | 1 | 1 | $0.15 | $0.15 | $0.15 | https://www.digikey.ca/en/products/detail/stackpole-electronics-inc/CF18JT1K00/1741612
A05 | 10 uF capacitor |  |  | TDK Corporation | digikey | 1 | 1 | 1 | $0.86 | $0.86 | $0.86 | https://www.digikey.ca/en/products/detail/tdk-corporation/FG24X7R1A106KRT06/5802984
A06 | LM4931 Voltage Regulator | Linear 5V 250MA |  | STMicroelectronics | digikey | 1 | 1 | 1 | $1.43 | $1.43 | $1.43 | https://www.digikey.ca/en/products/detail/stmicroelectronics/L4931CZ50-AP/1038130
A07 | STEMMA QT Cable - 50mm |  |  | SparkFun Electronics | digikey | 1 | 1 | 1 | $1.53 | $1.53 | $1.53 | https://www.digikey.ca/en/products/detail/sparkfun-electronics/PRT-17260/13629028
A08 | Adafruit MPR121 Touch Sensor | 12-Key Capacitive Sensor with STEMMA QT |  | Adafruit Industries LLC | digikey | 1 | 1 | 1 | $11.45 | $11.45 | $11.45 | https://www.digikey.ca/en/products/detail/adafruit-industries-llc/1982/4990787?gad_source=1
A09 | Copper Tape |  |  | Adafruit Industries LLC | digikey | 1 | 1 | 1 | $7.13 | $7.13 | $7.13 | https://www.digikey.ca/en/products/detail/adafruit-industries-llc/3483/9745247
A10 | Speaker | 4 Ohm 3W 100 Hz ~ 20 kHz |  | Ole Wolff Electronics Inc | digikey | 1 | 1 | 1 | $4.64 | $4.64 | $4.64 | https://www.digikey.ca/en/products/detail/ole-wolff-electronics-inc/OWS-4021TA-4/16735143
A11 | Push Button | 0.05A 12 V through hole |  | Same Sky | digikey | 2 | 1 | 2 | $0.15 | $0.30 | $0.30 | https://www.digikey.ca/en/products/detail/same-sky-formerly-cui-devices/TS02-66-100-BK-160-SCR-D/15634282
A12 | Slide Switch | 200MA 30 V |  | E-Switch | digikey | 1 | 1 | 1 | $1.28 | $1.28 | $1.28 | https://www.digikey.ca/en/products/detail/e-switch/EG1206A/251334
A13 | microSD card | DFPlayer takes max 32 GB |  | SIRIMAL | Amazon | 1 | 1 | 1 | $6.99 | $6.99 | $6.99 | https://www.amazon.ca/Class-Memory-Cards-Micro-Card/dp/B0DC1VMKS8
A14 | M3 x 8 mm screws |  |  | Keystone Electronics | digikey | 5 | 1 | 5 | $0.31 | $1.55 | $1.55 | https://www.digikey.ca/en/products/detail/keystone-electronics/9907/317328?productid=317328&gad_source=1
A15 | 24 AWG wire |  |  | TE Connectivity Raychem Cable Protection | digikey | 1 | 1 | 1 | $1.80 | $1.80 | $1.80 | https://www.digikey.ca/en/products/detail/te-connectivity-raychem-cable-protection/55A0111-24-9/2399803
A16 | Battery Spring | Compatible with AAA batteries |  | Keystone Electronics | digikey | 1 | 1 | 1 | $0.42 | $0.42 | $0.42 | https://www.digikey.ca/en/products/detail/keystone-electronics/5201/316365
A17 | Battery Plate | Compatible with AAA batteries |  | Keystone Electronics | digikey | 1 | 1 | 1 | $0.22 | $0.22 | $0.22 | https://www.digikey.ca/en/products/detail/keystone-electronics/5223/316374
A18 | Battery Bridge Plate | Compatible with AAA batteries |  | Keystone Electronics | digikey | 1 | 1 | 1 | $0.58 | $0.58 | $0.58 | https://www.digikey.ca/en/products/detail/keystone-electronics/5213/316372
 | Solder |  |  | Chip Quik Inc. | digikey | 1 | 1 | 1 | $10.62 | $10.62 | $10.62 | https://www.digikey.ca/en/products/detail/chip-quik-inc./RASWLF.031%25201OZ/9681997?productid=9681997&gad_source=1
 | AAA Batteries | Alkaline Batteries |  | Energizer | digikey | 4 | 4 | 1 | $5.45 | $5.45 | $5.45 | https://www.digikey.ca/en/products/detail/energizer-battery-company/E92/7400190?productid=7400190&gad_source=1
 |  | Shipping (flat rate for digikey) |  |  | digikey | 1 | 1 | 1 | $8.00 | $8.00 | $8.00
 | 3D Printed Parts |  |  |  |  |  |  | 101 |  | $2.53 | $2.53
 | Part | Description | Filament Type | Filament | Color | QTY / Device | Mass (g) / Part | Total Mass | $ / kg | $ / Device | Total Estimated Cost | Link
A19 | Electronic Tube Half | Device tube half holding electronics | PLA |  | Any | 1 | 34 | 34 | $25.00 | $0.85 | $0.85
A20 | Battery Tube Half | Device tube half holding batteries | PLA |  | Any | 1 | 43 | 43 | $25.00 | $1.08 | $1.08
A21 | Battery Cap | Cap that holds batteries in place | PLA |  | Any | 1 | 1 | 1 | $25.00 | $0.03 | $0.03
A22 | MPR121 Clip | Attaches MPR121 to electronic tube half | PLA |  | Any | 1 | 3 | 3 | $25.00 | $0.08 | $0.08
A23 | Speaker End Cap | End cap that covers speaker | PLA |  | Any | 1 | 11 | 11 | $25.00 | $0.28 | $0.28
A24 | Switch End Cap | End cap that covers switch/buttons | PLA |  | Any | 1 | 9 | 9 | $25.00 | $0.23 | $0.23
 | Tools
 | Tool | Description |  | Manufacturer | Supplier |  |  |  |  |  |  | Link
T01 | Philips Screwdriver | For screwing/ unscrewing device screws |  | Wera | Amazon |  |  |  |  |  |  | https://www.amazon.ca/Wera-05008725002-Kraftform-Phillips-Screwdriver/dp/B0035YLT08
T02 | Wire Strippers | For stripping wire |  | Hakko | Amazon |  |  |  |  |  |  | https://www.amazon.ca/Hakko-CSP-30-1-Stripper-Maximum-Capacity/dp/B00FZPHMUG
T03 | Flush Cutters | For trimming leads |  | Hakko | Amazon |  |  |  |  |  |  | https://www.amazon.ca/AstroAI-Digital-Multimeter-2000Counts-Voltage/dp/B01ISAMUA6
T04 | Needle Nose Pliers | For installing battery clips and wiring |  | Craftsman | Amazon |  |  |  |  |  |  | https://www.amazon.ca/CRAFTSMAN-CMHT81644-Long-Nose-PLIER-6IN/dp/B09JB2HS1D
T05 | Soldering Iron | For soldering electronic components |  | Vastar | Amazon |  |  |  |  |  |  | https://www.amazon.ca/Vastar-Soldering-Iron-Anti-Static-Off/dp/B07RZV2DW8?cv_ct_cx=soldering%2Biron&sbo=RZvfv%2F%2FHxDF%2BO5021pAnSA%3D%3D
T06 | Multimeter | For device testing |  | AstroAI | Amazon |  |  |  |  |  |  | https://www.amazon.ca/AstroAI-Digital-Multimeter-2000Counts-Voltage/dp/B01ISAMUA6
T07 | Scissors | For cutting copper tape |  | Scotch | Amazon |  |  |  |  |  |  | https://www.amazon.ca/Scotch-Multi-Purpose-Scissors-1-Pack-1428ESF/dp/B00GGBHT6U
 | Alternatives
 | Part | Description |  | Manufacturer | Supplier | QTY / Device | QTY / PKG | PKGs | $/ PKG | $ / Device | Total Estimated Cost | Link
A08 | Adafruit MPR121 Touch Sensor | Order from Adafruit website if digikey sold out |  | Adafruit Industries | Adafruit | 1 | 1 | 1 | $10.76 | $10.76 | $10.76 | https://www.adafruit.com/product/1982

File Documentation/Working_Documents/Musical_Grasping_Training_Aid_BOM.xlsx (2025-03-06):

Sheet: BOM
Device: | Musical Grasping Training Aid
Version: | V1.1
Last Updated: | 2025-Mar-06
 |  |  |  |  |  |  |  | Total filament (g) |  | Unit Cost | Total Estimated Cost
 |  |  |  |  |  |  |  | 101 |  | $79.86 | $79.86
ID | Commercial Parts |  |  |  |  |  |  |  |  | $77.33 | $77.33
 | Part | Description | Part Number | Manufacturer | Supplier | QTY / Device | QTY / PKG | PKGs | $/ PKG | $ / Device | Total Estimated Cost | Link
A01 | 30x70mm Proto Board |  | 1528-4784-ND | Adafruit Industries LLC | digikey | 1 | 1 | 1 | $4.25 | $4.25 | $4.25 | https://www.digikey.ca/en/products/detail/adafruit-industries-llc/4784/13617526
A02 | Adafruit QT Py microcontroller | SAMD21 with STEMMA QT | 1528-4600-ND | Adafruit Industries LLC | digikey | 1 | 1 | 1 | $10.80 | $10.80 | $10.80 | https://www.digikey.ca/en/products/detail/adafruit-industries-llc/4600/13543375
A03 | DFRobot DFPlayerMini | Mini MP3 Player | 1738-1041-ND | DFRobot | digikey | 1 | 1 | 1 | $8.50 | $8.50 | $8.50 | https://www.digikey.ca/en/products/detail/dfrobot/DFR0299/6588463
A04 | 1K Ohm Resistor |  | CF18JT1K00CT-ND | Stackpole Electronics Inc | digikey | 1 | 1 | 1 | $0.15 | $0.15 | $0.15 | https://www.digikey.ca/en/products/detail/stackpole-electronics-inc/CF18JT1K00/1741612
A05 | 10 uF capacitor |  | 445-173370-1-ND | TDK Corporation | digikey | 1 | 1 | 1 | $0.86 | $0.86 | $0.86 | https://www.digikey.ca/en/products/detail/tdk-corporation/FG24X7R1A106KRT06/5802984
A06 | LM4931 Voltage Regulator | Linear 5V 250MA | 497-5838-1-ND | STMicroelectronics | digikey | 1 | 1 | 1 | $1.43 | $1.43 | $1.43 | https://www.digikey.ca/en/products/detail/stmicroelectronics/L4931CZ50-AP/1038130
A07 | STEMMA QT Cable - 50mm |  | 1568-PRT-17260-ND | SparkFun Electronics | digikey | 1 | 1 | 1 | $1.53 | $1.53 | $1.53 | https://www.digikey.ca/en/products/detail/sparkfun-electronics/PRT-17260/13629028
A08 | Adafruit MPR121 Touch Sensor | 12-Key Capacitive Sensor with STEMMA QT | 1528-1038-ND | Adafruit Industries LLC | digikey | 1 | 1 | 1 | $11.45 | $11.45 | $11.45 | https://www.digikey.ca/en/products/detail/adafruit-industries-llc/1982/4990787
A09 | Copper Tape |  | 1528-2748-ND | Adafruit Industries LLC | digikey | 1 | 1 | 1 | $7.13 | $7.13 | $7.13 | https://www.digikey.ca/en/products/detail/adafruit-industries-llc/3483/9745247
A10 | Speaker | 4 Ohm 3W 100 Hz ~ 20 kHz | 3949-OWS-4021TA-4-ND | Ole Wolff Electronics Inc | digikey | 1 | 1 | 1 | $4.64 | $4.64 | $4.64 | https://www.digikey.ca/en/products/detail/ole-wolff-electronics-inc/OWS-4021TA-4/16735143
A11 | Push Button | 0.05A 12 V through hole | 2223-TS02-66-100-BK-160-SCR-D-ND | Same Sky | digikey | 2 | 1 | 2 | $0.15 | $0.30 | $0.30 | https://www.digikey.ca/en/products/detail/same-sky-formerly-cui-devices/TS02-66-100-BK-160-SCR-D/15634282
A12 | Slide Switch | 200MA 30 V | EG1917-ND | E-Switch | digikey | 1 | 1 | 1 | $1.28 | $1.28 | $1.28 | https://www.digikey.ca/en/products/detail/e-switch/EG1206A/251334
A13 | microSD card | DFPlayer takes max 32 GB | 1597-112990066-ND | Seeed Technology Co. | digikey | 1 | 1 | 1 | $6.99 | $6.99 | $6.99 | https://www.digikey.ca/en/products/detail/seeed-technology-co-ltd/112990066/10290294
A14 | M3 x 8 mm screws |  | 36-9907-ND | Keystone Electronics | digikey | 5 | 1 | 5 | $0.31 | $1.55 | $1.55 | https://www.digikey.ca/en/products/detail/keystone-electronics/9907/317328
A15 | 24 AWG wire |  | 484-55A0111-24-9-DS-ND | TE Connectivity Raychem Cable Protection | digikey | 1 | 1 | 1 | $1.80 | $1.80 | $1.80 | https://www.digikey.ca/en/products/detail/te-connectivity-raychem-cable-protection/55A0111-24-9/2399803
A16 | Battery Spring | Compatible with AAA batteries | 36-5201-ND | Keystone Electronics | digikey | 1 | 1 | 1 | $0.42 | $0.42 | $0.42 | https://www.digikey.ca/en/products/detail/keystone-electronics/5201/316365
A17 | Battery Plate | Compatible with AAA batteries | 36-5223-ND | Keystone Electronics | digikey | 1 | 1 | 1 | $0.22 | $0.22 | $0.22 | https://www.digikey.ca/en/products/detail/keystone-electronics/5223/316374
A18 | Battery Bridge Plate | Compatible with AAA batteries | 36-5213-ND | Keystone Electronics | digikey | 1 | 1 | 1 | $0.58 | $0.58 | $0.58 | https://www.digikey.ca/en/products/detail/keystone-electronics/5213/316372
 | AAA Batteries | Alkaline Batteries | E92-ND | Energizer | digikey | 4 | 4 | 1 | $5.45 | $5.45 | $5.45 | https://www.digikey.ca/en/products/detail/energizer-battery-company/E92/7400190
 |  | Shipping (flat rate for digikey) |  |  | digikey | 1 | 1 | 1 | $8.00 | $8.00 | $8.00
 | 3D Printed Parts |  |  |  |  |  |  | 101 |  | $2.52 | $2.52
 | Part | Description | Filament Type | Filament | Color | QTY / Device | Mass (g) / Part | Total Mass | $ / kg | $ / Device | Total Estimated Cost | Link
A19 | Electronic Tube Half | Device tube half holding electronics | PLA |  | Any | 1 | 34 | 34 | $25.00 | $0.85 | $0.85
A20 | Battery Tube Half | Device tube half holding batteries | PLA |  | Any | 1 | 43 | 43 | $25.00 | $1.07 | $1.07
A21 | Battery Cap | Cap that holds batteries in place | PLA |  | Any | 1 | 1 | 1 | $25.00 | $0.03 | $0.03
A22 | MPR121 Clip | Attaches MPR121 to electronic tube half | PLA |  | Any | 1 | 3 | 3 | $25.00 | $0.08 | $0.08
A23 | Speaker End Cap | End cap that covers speaker | PLA |  | Any | 1 | 11 | 11 | $25.00 | $0.28 | $0.28
A24 | Switch End Cap | End cap that covers switch/buttons | PLA |  | Any | 1 | 9 | 9 | $25.00 | $0.23 | $0.23
 | Tools
 | Tool | Description |  | Manufacturer | Supplier |  |  |  |  |  |  | Link
T01 | Philips Screwdriver | For screwing/ unscrewing device screws |  | Wera | Amazon |  |  |  |  |  |  | https://www.amazon.ca/Wera-05008725002-Kraftform-Phillips-Screwdriver/dp/B0035YLT08
T02 | Wire Strippers | For stripping wire |  | Hakko | Amazon |  |  |  |  |  |  | https://www.amazon.ca/Hakko-CSP-30-1-Stripper-Maximum-Capacity/dp/B00FZPHMUG
T03 | Flush Cutters | For trimming leads |  | Hakko | Amazon |  |  |  |  |  |  | https://www.amazon.ca/AstroAI-Digital-Multimeter-2000Counts-Voltage/dp/B01ISAMUA6
T04 | Needle Nose Pliers | For installing battery clips and wiring |  | Craftsman | Amazon |  |  |  |  |  |  | https://www.amazon.ca/CRAFTSMAN-CMHT81644-Long-Nose-PLIER-6IN/dp/B09JB2HS1D
T05 | Soldering Iron | For soldering electronic components |  | Vastar | Amazon |  |  |  |  |  |  | https://www.amazon.ca/Vastar-Soldering-Iron-Anti-Static-Off/dp/B07RZV2DW8?cv_ct_cx=soldering%2Biron&sbo=RZvfv%2F%2FHxDF%2BO5021pAnSA%3D%3D
T06 | Multimeter | For device testing |  | AstroAI | Amazon |  |  |  |  |  |  | https://www.amazon.ca/AstroAI-Digital-Multimeter-2000Counts-Voltage/dp/B01ISAMUA6
T07 | Scissors | For cutting copper tape |  | Scotch | Amazon |  |  |  |  |  |  | https://www.amazon.ca/Scotch-Multi-Purpose-Scissors-1-Pack-1428ESF/dp/B00GGBHT6U
 | Solder |  | RASWLF.0311OZ-ND | Chip Quik Inc. | digikey | 1 | 1 | 1 | 10.62 | 10.62 | 10.62 | https://www.digikey.ca/en/products/detail/chip-quik-inc./RASWLF.031%25201OZ/9681997
 | Alternatives
 | Part | Description |  | Manufacturer | Supplier | QTY / Device | QTY / PKG | PKGs | $/ PKG | $ / Device | Total Estimated Cost | Link
A08 | Adafruit MPR121 Touch Sensor | Order from Adafruit website if digikey sold out |  | Adafruit Industries | Adafruit | 1 | 1 | 1 | $10.76 | $10.76 | $10.76 | https://www.adafruit.com/product/1982

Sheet: Digikey
Part ID | Digikey Part Number | Qty
A01 | 1528-4784-ND | 1
A02 | 1528-4600-ND | 1
A03 | 1738-1041-ND | 1
A04 | CF18JT1K00CT-ND | 1
A05 | 445-173370-1-ND | 1
A06 | 497-5838-1-ND | 1
A07 | 1568-PRT-17260-ND | 1
A08 | 1528-1038-ND | 1
A09 | 1528-2748-ND | 1
A10 | 3949-OWS-4021TA-4-ND | 1
A11 | 2223-TS02-66-100-BK-160-SCR-D-ND | 2
A12 | EG1917-ND | 1
A13 | 1597-112990066-ND | 1
A14 | 36-9907-ND | 5
A15 | 484-55A0111-24-9-DS-ND | 1
A16 | 36-5201-ND | 1
A17 | 36-5223-ND | 1
A18 | 36-5213-ND | 1

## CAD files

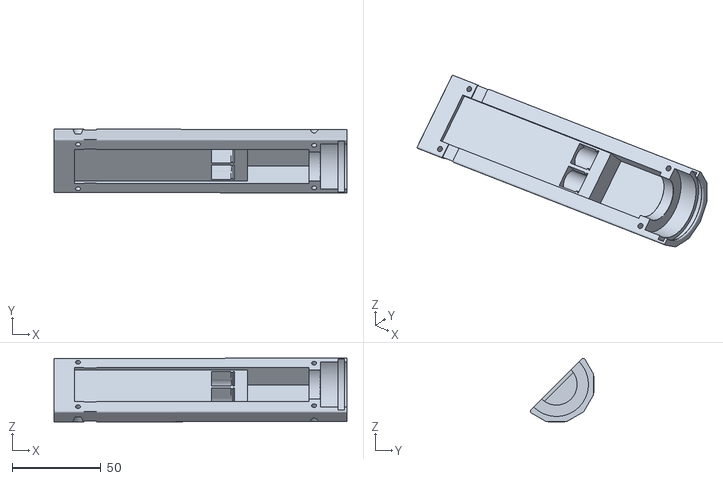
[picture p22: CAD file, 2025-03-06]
Build_Files/3D_Printing_Files/MGTA_Battery_Tube_Half.stl
165.0 x 35.8 x 35.8

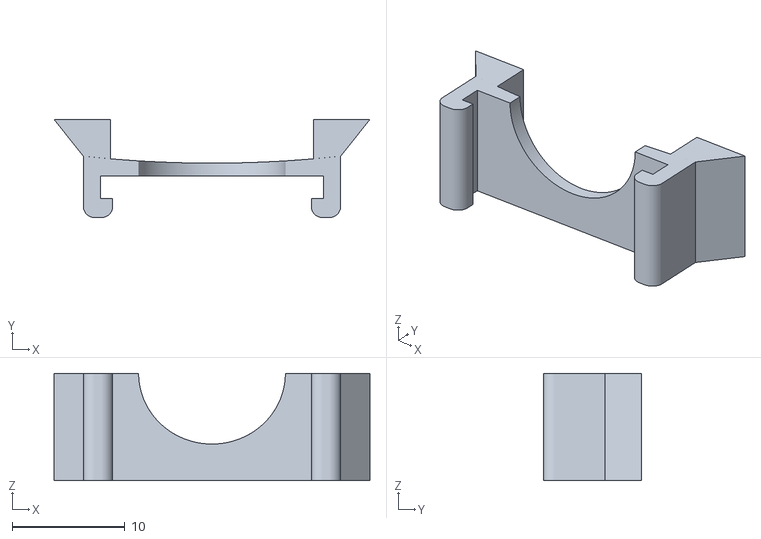
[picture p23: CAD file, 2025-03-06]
Build_Files/3D_Printing_Files/MGTA_MPR121_Clip.stl
28.0 x 8.70 x 9.50

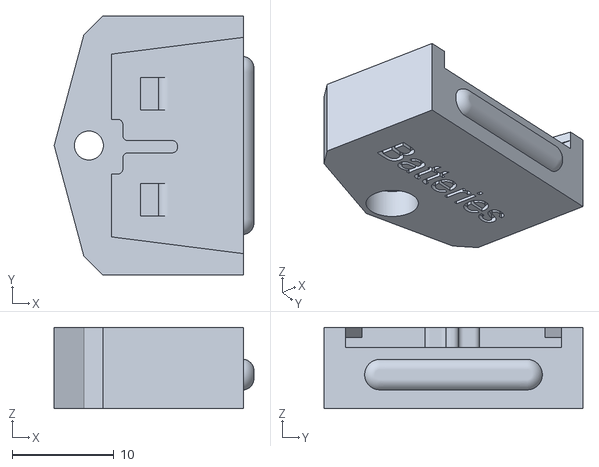
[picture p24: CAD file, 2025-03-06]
Build_Files/3D_Printing_Files/MGTA_Battery_Clip.stl
19.7 x 25.5 x 8.00

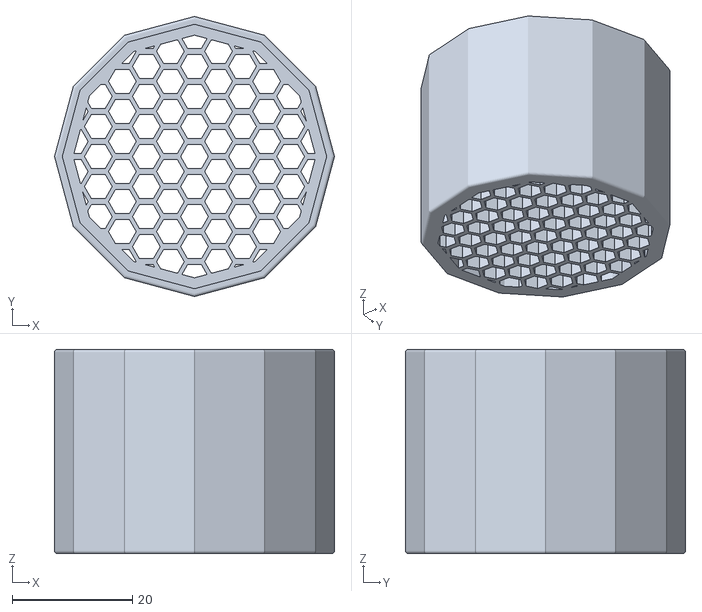
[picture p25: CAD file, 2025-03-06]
Build_Files/3D_Printing_Files/MGTA_Speaker_End_Cap.stl
46.6 x 46.6 x 34.0

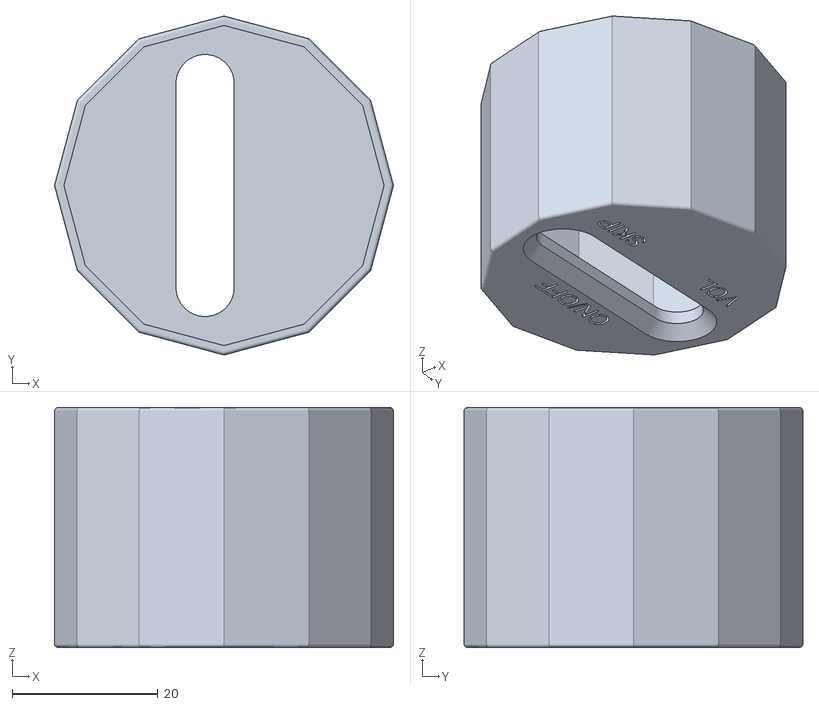
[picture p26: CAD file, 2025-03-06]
Build_Files/3D_Printing_Files/MGTA_Switch_End_Cap.stl
46.6 x 46.6 x 33.0

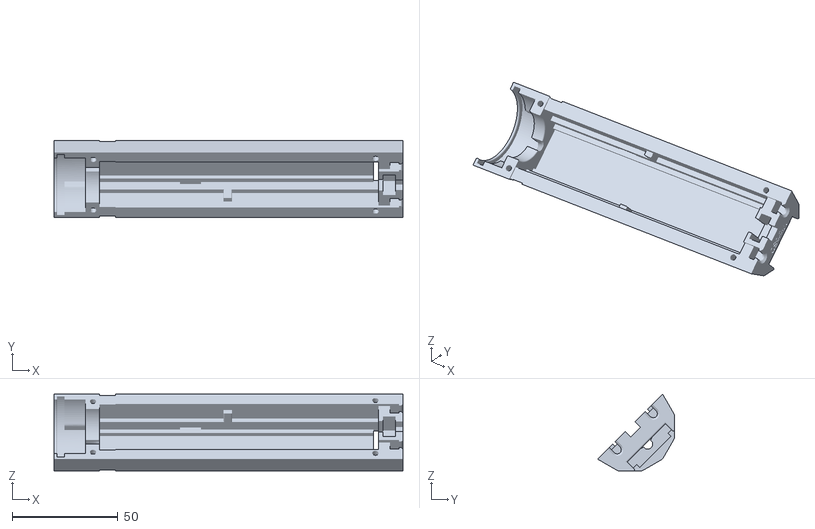
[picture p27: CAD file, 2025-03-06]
Build_Files/3D_Printing_Files/MGTA_Electronics_Tube_Half.stl
165.0 x 36.4 x 36.4

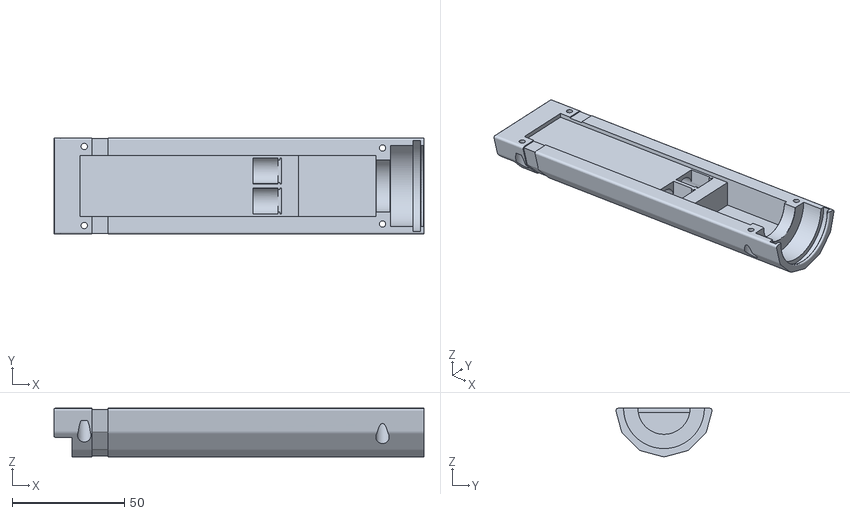
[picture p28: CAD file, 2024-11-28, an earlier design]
Old/Build_Files/3D_Printing_Files/MGTA_Battery_Tube_Half.stl
165.0 x 42.9 x 21.6

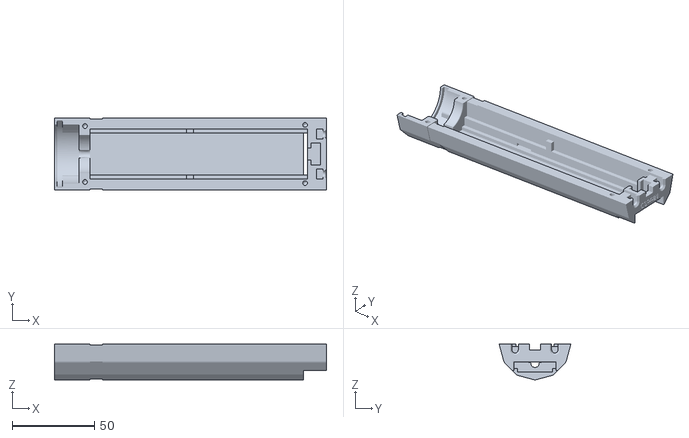
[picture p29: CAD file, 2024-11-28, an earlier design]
Old/Build_Files/3D_Printing_Files/MGTA_Electronics_Tube_Half.stl
165.0 x 43.5 x 21.6

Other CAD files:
Old/Build_Files/3D_Printing_Files/MGTA_Switch_End_Cap.stl
Old/Build_Files/3D_Printing_Files/MGTA_Speaker_End_Cap.stl
Old/Build_Files/3D_Printing_Files/MGTA_MPR121_Clip.stl
Old/Build_Files/3D_Printing_Files/MGTA_Battery_Clip.stl
Design_Files/CAD_Files/MGTA/Battery_Cap.f3d
Design_Files/CAD_Files/MGTA/Battery_Tube_Half.f3d
Design_Files/CAD_Files/MGTA/Electronics_Tube_Half.f3d
Design_Files/CAD_Files/MGTA/MPR121_Clip.f3d
Design_Files/CAD_Files/MGTA/Speaker_End_Cap.f3d
Design_Files/CAD_Files/MGTA/Switch_End_Cap.f3d

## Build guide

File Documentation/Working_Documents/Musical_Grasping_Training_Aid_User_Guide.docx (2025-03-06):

# Overview

This document contains the necessary information to use the Musical Grasping Training Aid, a device that motivates an individual to pick up and hold it by playing music while the object is being held.

A picture of the Grasping Musical Training Aid from the side. The device is a hexagonal prism with copper tape strips along the body of the device. There are two blue end caps on the device.

## Introduction

The Musical Grasping Training Aid is designed to promote grasping and holding. When a person holds the device, it plays music and when the device is not being held, it pauses the music. Users can upload their own music onto a microSD card inside the device and upload new or additional songs when no longer motivated by the current selection of songs.

The training aid senses when it is being grasped using a conductive activation surface created by strips of copper tape along the device’s outer surface. Users must be touching the copper tape for the device to play music.

## Features

Number | Feature | Functionality
1 | Speaker | Plays music
2 | Speaker End Cap | Covers the speaker
3 | Conductive Tape | Senses grasp and activates music (activation surface)
4 | Volume Button | Cycles through volume levels
5 | On/Off Switch | Turns device on/off
6 | Switch End Cap | Covers switch, buttons, battery cap and microSD card slot
7 | Skip Button | Skips through the music files uploaded on microSD card
8 | Battery Cap | Provides access to device batteries
9 | MicroSD Slot | Provides access to microSD card for music file upload

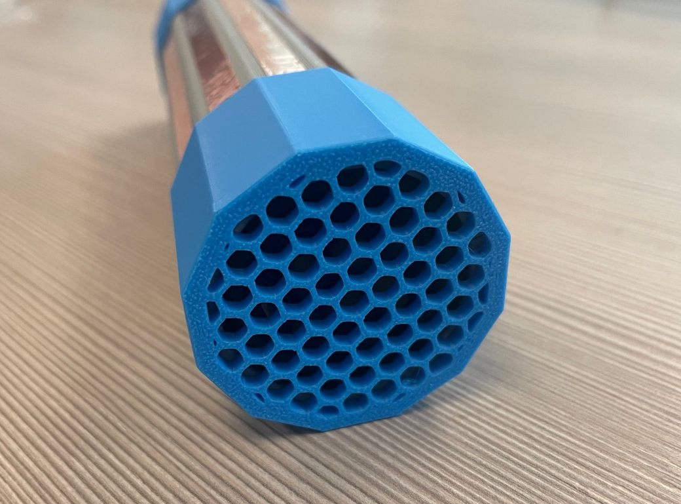
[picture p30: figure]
A side angle view of the Musical Grasping Training Aid displaying a blue speaker end cap on the device.

2

3

1

1

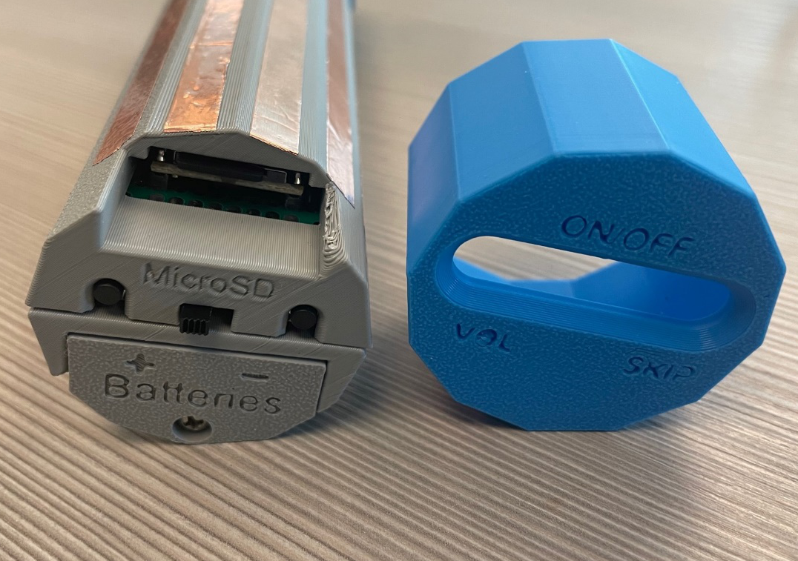
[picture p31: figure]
A silver cylindrical device with copper tape strips, two pushbuttons, battery compartment and microSD card insert. There is a blue switch end cap to the side of the device.

6

8

4

7

5

9

The Musical Grasping Training Aid is a long tube, with two capped ends. The speaker is located on the end with the honeycomb pattern, and there is a power switch, a volume and song skip button on the other end cap. Underneath this switch end cap, there is battery cap which provides access to the batteries. There are twelve strips of copper tape along the outside of the device enclosure which forms the activation surface for song play. When the training aid is on and someone is touching the copper tape activation surface, the device will start playing the first song that was uploaded to the microSD card. When you stop touching the copper tape activation surface, the device will stop playing music.

The device will always start playing the first song loaded onto the microSD card after it is turned on. If the toy is held for the entire duration of the first song, it will start playing the next song uploaded to the microSD card. The toy will continue to loop through all the songs on the microSD card, resetting anytime it is turned off and on again.

The buttons located on the side of the device allow for volume control and song skip feature. The left volume button will cycle through different volume settings and the right song skip button allows you to play the next song onto the microSD card.

## Specifications

Item | Musical Grasping Training Aid
Length | 165 mm
Diameter | 43 mm
Music Upload | microSD card (different storage options available)
Mass [g] | 200 g
Power | 4 x AAA Batteries

## Compatibility

The Musical Grasping Training Aid currently has no compatibility with other devices and is used as a standalone device.

## Usage

### Power On

To power on the device, flip the switch on the side of the device from OFF to ON.

### Calibration

After turning on the power switch, wait 10 seconds for the device to calibrate. To properly calibrate the device, make sure it is placed in the Musical Grasping Training Aid stand or held by the two end caps, and it is not being touched.

### Playing Music

To play music, the device needs to be grasped along the copper tape along the tube body. The toy will play music while it is being held and stop playing music when it is no longer being held. Once the device is grasped again, the music will resume playing where it stopped.

Use the slide switch to turn the toy off when not in use.

### Volume Control

To change the volume of the music being played, press the left button on the side of the device (above the VOL label). The device has six volume levels (5, 8, 11, 14, 17, 20), and each press of the button cycles to the next volume setting. When calibrated, the device starts at level 5 and will cycle through the remaining levels. If the volume button is pressed while the device is playing music at the last level, it will restart to play music at the first volume level.

### Song Skip

To skip a song, press the right button on the side of the device (above the SKIP label). This will skip to the next song loaded onto the microSD card inside the device. If the skip button is pressed while the last song is played, the device restarts the song list and plays the first song.

### Uploading Songs

To upload songs onto the device, turn off the power switch and gently pull off the switch end cap. Once the end cap is removed, gently push the card from the reader as indicated by the arrow until you hear/feel a click. The microSD card will then slightly pop out of the reader, and you can gently pull it out. Connect the microSD card to your computer (microSD card adapter may be required).

When uploading songs, the files must be uploaded using a specific format, order and naming convention to work properly.

Step 1. Ensure that the songs are in .mp3 format. If your music files are not in.mp3 format, you can use an online mp3 converter to correctly format your music files.

Step 2. Upload songs one at a time. The order in which the songs are uploaded is the order the device will play the songs (i.e. the first song uploaded will be the first song to play).

Step 3. Name the song files using the correct naming convention. The DFPlayer Mini requires that all files follow a specific naming convention to play in the correct order. First, create a folder labeled “mp3” on a microSD card. Then copy the music files one by one inside the folder in the desired playing order. Each song file must be renamed to start with 4 digits, ranging from 0001-9999. After the last number, the song file may be named (i.e. a song file named “[SongName].mp3” would need to be titled “0001[SongName].mp3”).

Note: It is important that the songs are named in ascending order from 0001 to 9999 in the order they were uploaded onto the microSD card. When copying the files into the folder, time stamps are created which may result in no music being played if the timestamps do not match with the track numbers.

After uploading all the song files, hover your computer mouse over the USB tab along the left side of the panel in File Explorer. Press and hold the left mouse key and drag it into the “mp3” folder and let go of the mouse key. This will create a shortcut to the USB which will allow the songs to loop once they have been played. Once all songs are uploaded, insert the card back into the training aid by pressing it into the reader until it clicks and locks back in place. Turn the toy back on and grasp the device to play the new music.

### Changing Batteries

The replace the batteries, turn the device off and remove the switch end cap. Once the end cap is removed, use a Philips screwdriver to remove the battery cap allowing access to the four AAA batteries inside. Tilt the device to slide out the old batteries and insert the new batteries. Pay attention to the positive and negative label on the battery cap to ensure that batteries are correctly placed inside the device. Secure the battery cap back on using the screw and put the end cap back on.

## Care

The Musical Grasping Training Aid is made of 3D printed plastic. Exposure to high heat may cause warping and/or negatively affect function. Extended exposure to sunlight will also weaken the plastic on the device.

The device contains electronics and is not waterproof. If the device becomes wet, make sure it is off and do not use it until it has completely dried. It may help to open any electronic enclosures to speed up drying and ensure it has completely dried.

### Cleaning

The Musical Grasping Training Aid can be wiped with a damp cloth. Do not use hot water or clean in a dishwasher. The device is not waterproof and will be damaged if submerged under water.

## Troubleshooting

### Music Not Playing

Music doesn’t play when device is grasped.

- Double check to make sure the song files are uploaded to the microSD card using the correct naming convention. Refer to the “Uploading Songs” section above.
- Double check speaker connections inside the device. To do this, pull the endcaps off the device and unscrew the four screws located along the body of the device. Once removed, gently open the device, making sure not to pull apart any wiring and lay the two halves side by side on a flat surface. Gently remove the power switch and two pushbuttons from their inserts and then remove the protoboard, MPR121 sensor and speaker out of the device enclosure. Place all the electrical components on a flat service, making sure you can see the circuit. Note that the battery connections will still be attached to one side of the device enclosure and do not need to be removed. Double check all the solder joints and wiring connections as shown in the Maker Guide.
- Make sure microSD card is inserted.

## Disposal

Disassemble the Musical Grasping Training Aid and separate out the recyclable and compostable components, and those that must be thrown out. Electronics and batteries should be disposed of following your local waste management guidelines.

PLA filament may be industrially compostable in your area. Check with your waste management company if PLA can be composted or must be thrown in the garbage.

© 2024-2025 by Neil Squire This work is licensed under the CC BY SA 4.0 License: http://creativecommons.org/licenses/by-sa/4.0 Files available at https://github.com/makersmakingchange/Musical_Grasping_Training_Aid Page 2 of 3

V 1.0 | MARCH 2025 Musical Grasping Training Aid user Guide

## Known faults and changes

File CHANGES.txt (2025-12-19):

Version 1.1 | 2025-Dec-18
 - Modified firmware to explicitly enable automatic calibration after sensor library change.

Version 1.0 | 2024-Sep-16
 - Added a skip song and volume button
 - Added battery compartment to allow for battery replacement
 - Added slot to access microSD and update/change music files
 - Updated software to incorporate volume and skip song buttons
 - Redesigned the CAD to accommodate updated user interface
 - Created and updated standard MMC documentation

Version 0.3 | 
 - Initial Device
	- On/Off Switch
	- Speaker
	- Adafruit QT Py SAMD21 Microcontroller
	- Adafruit MPR121 Capacitive Touch Sensor
	- DFRobot DFPlayer Mini 
	- 4 AAA Batteries (sealed inside device)
	- microSD card (sealed inside device)
 - Starts playing first song when grasped and pauses when let go
 - Song uploaded during assembly and cannot be changed

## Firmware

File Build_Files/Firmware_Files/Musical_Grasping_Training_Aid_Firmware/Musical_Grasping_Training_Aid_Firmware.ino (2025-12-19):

/*
 * Musical_Grasping_Training_Aid_Firmware (v1.0) 
 * 
 * Copyright 2024 Neil Squire/Makers Making Change. 
 * 
 * License: This work is distributed under the terms of the GNU General Public License.
 * 
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
 * This program is distributed in the hope that it will be useful, but WITHOUT ANY WARRANTY; 
 * without even the implied warranty of MERCHANTABILITY or FITNESS FOR A PARTICULAR PURPOSE. 
 * See the GNU General Public License for more details.
 * 
 * You should have received a copy of the GNU General Public License along with this program. 
 * If not, see <https://www.gnu.org/licenses/>.
 */


#include <Arduino.h>
#include <Wire.h>
#include <DFRobotDFPlayerMini.h>  // MP3 reader library
#include "Adafruit_MPR121.h"      // Capacitive Touch Sensor library

#ifndef _BV
#define _BV(bit) (1 << (bit))
#endif

DFRobotDFPlayerMini myDFPlayer;           // Create  DFPlayer object
Adafruit_MPR121 cap = Adafruit_MPR121();  // Create MPR121 object

uint16_t currtouched = 0;  // Variable to store capacitance value from MPR121

const int buttonPin1 = A0;  // Pin for pushbutton 1
const int buttonPin2 = A1;  // Pin for pushbutton 2

const int presetVolumes[] = { 5, 8, 11, 14, 17, 20 };  // Preset volume levels
int currentVolumeIndex = 0;                            // Volume index counter
int currentSongIndex = 0;                              // Song index counter

int buttonState1 = 0;  // Variable to store button 1 state
int buttonState2 = 0;  // Variable to store button 2 state

void setup() {

  pinMode(buttonPin1, INPUT_PULLUP);  // Set buttonPin1 as an input
  pinMode(buttonPin2, INPUT_PULLUP);  // Set buttonPin2 as an input

  Serial.begin(115200);  //Setup Serial communication; baud rate is 9600 bps
  Serial.println("Entering Setup");

  //Wire.begin(); //Initialize I2C communication

  Serial1.begin(9600);        // Setup Serial1 communication; baud rate is 9600 bps
  while (!Serial) delay(10);  // Wait for Serial1 to initialize
  //---MPR121 Capacitive Touch Sensor Test----
  Serial.println("Adafruit MPR121 Capacitive Touch Sensor Test");

  // Default address is 0x5A, if tied to 3.3V its 0x5B
  // If tied to SDA its 0x5C and if SCL then 0x5D

  if (!cap.begin(0x5A)) {
    Serial.println("MPR121 not found, check wiring?");
    while (true)
      ;
  }
  Serial.println("MPR121 found!");
  cap.setAutoconfig(true);  // Enable auto calibration for capacitive sensor

  //---DFPlayer Test----
  Serial.println("DFRobot DFPlayer Test");
  if (!myDFPlayer.begin(Serial1)) {  // Use Serial1 to communicate with the DFPlayer
    Serial.println(F("Unable to begin:"));
    Serial.println(F("1.Please recheck the connection!"));
    Serial.println(F("2.Please insert the SD card!"));
    while (true)
      ;
  }
  Serial.println(F("DFPlayer Mini online."));

  //----Set volume----
  myDFPlayer.volume(presetVolumes[currentVolumeIndex]);  //Set volume value to currentVolumeIndex which corresponds to the first volume setting
  myDFPlayer.volumeUp();                                 //Volume Up
  myDFPlayer.volumeDown();                               //Volume Down
  myDFPlayer.EQ(DFPLAYER_EQ_NORMAL);                     //Set Equalizer
  myDFPlayer.outputDevice(DFPLAYER_DEVICE_SD);           //Set device (SD as default)
  myDFPlayer.enableLoopAll();                            //Loop files after play through once
  myDFPlayer.play(1);                                    //Play the first music file
  myDFPlayer.pause();                                    //Pause music
}

void loop() {

  currtouched = cap.touched();  //Read the current touched state
  Serial.println(currtouched);
  delay(500);  //Delay for 500 milliseconds

  if (currtouched > 1) {  //The value 1 is the threshold. Value can be changed to modify sensitivity
    myDFPlayer.start();   //start the mp3 from the pause
  } else {
    myDFPlayer.pause();  //pause the mp3
  }

  int buttonState1 = digitalRead(buttonPin1);  //Read value of skip song button
  int buttonState2 = digitalRead(buttonPin2);  //Read value of volume button


  //----Skip Song Button (Push Button 1)----
  if (buttonState1 == LOW) {  //If pushbutton 1 is pressed
    myDFPlayer.next();        //Play next song
    Serial.println("next:");
    Serial.print("Current track:");
    Serial.println(myDFPlayer.readCurrentFileNumber() + 1);
  }

  //----Volume Button (Push Button 2)----
  if (buttonState2 == LOW) {                               //If pushbutton 2 is pressed
    currentVolumeIndex = (currentVolumeIndex + 1) % 6;     // Cycle to next volume value
    myDFPlayer.volume(presetVolumes[currentVolumeIndex]);  // New volume value
    Serial.print("Set volume to ");
    Serial.println(presetVolumes[currentVolumeIndex]);
  }
}

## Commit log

2024-11-28 Updated CHANGES
    Includes changes for V0.3 and V1.0 changes
    [Battery_Cap.f3d, Battery_Tube_Half.f3d, Device_Name_BOM.xlsx, Electronics_Tube_Half.f3d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]
2024-11-28 Revert Commit
    [Battery_Cap.f3d, Battery_Tube_Half.f3d, Device_Name_BOM.xlsx, Electronics_Tube_Half.f3d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]
2025-03-06 Remove template placeholders
    [Device_Name_BOM.xlsx, OpenAT_Placard.f3d, OpenAT_Placard.stl]
2025-03-06 Add design files
    [Battery_Cap.f3d, Battery_Tube_Half.f3d, Electronics_Tube_Half.f3d, MPR121_Clip.f3d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]
2025-03-06 Add print files
    [MGTA_Battery_Clip.stl, MGTA_Battery_Tube_Half.stl, MGTA_Electronics_Tube_Half.stl, MGTA_MPR121_Clip.stl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]
2025-03-06 Add BOM
    [Musical_Grasping_Training_Aid_BOM.csv, Musical_Grasping_Training_Aid_BOM.xlsx]
2025-03-06 Update STLs to intended print orientation
    [MGTA_Battery_Clip.stl, MGTA_Battery_Tube_Half.stl, MGTA_Electronics_Tube_Half.stl, MGTA_MPR121_Clip.stl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]
2025-03-06 Update STLs
    Rotate to intended print orientation
    [MGTA_Battery_Clip.stl, MGTA_Battery_Tube_Half.stl, MGTA_Electronics_Tube_Half.stl, MGTA_MPR121_Clip.stl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]
2025-12-18 Enable auto calibration for MPR121 sensor
    Added cap.setAutoconfig(true) in setup() to enable automatic calibration for the Adafruit MPR121 capacitive touch sensor.

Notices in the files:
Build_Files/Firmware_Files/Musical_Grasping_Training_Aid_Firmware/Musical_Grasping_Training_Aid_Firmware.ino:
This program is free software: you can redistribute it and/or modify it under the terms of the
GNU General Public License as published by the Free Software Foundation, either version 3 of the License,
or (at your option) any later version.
